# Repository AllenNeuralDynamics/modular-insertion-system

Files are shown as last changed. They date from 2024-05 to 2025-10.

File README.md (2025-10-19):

# Modular Insertion System

A flexible, scalable extracellular electrophysiology rig

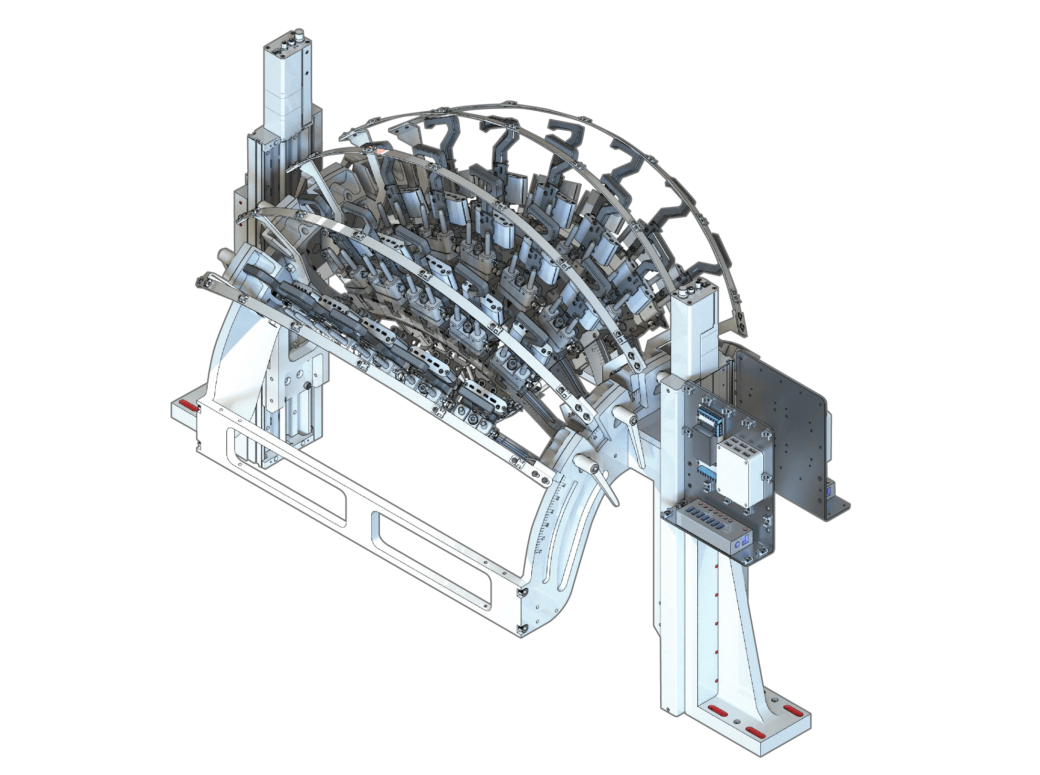
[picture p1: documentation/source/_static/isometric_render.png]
Rendering of the insertion system


## Key features

- Insertion angles up to ±75° A/P and ±45° M/L
- Modules for electrophysiology, optogenetics, and microscopes
- 600 mm x 500 mm open area for behavioral platform
- Design files available for noncommercial use

## Contributors

- Mechanical design: Jon Arnold
- Concept and oversight: Josh Siegle, Karel Svoboda
- Validation: Galen Lynch, Yoni Browning, Anna Lakunina, Xinxin Yin, Han Hou, Susu Chen
- Electrical design: Sonya Vasquez

## How to order

In most cases, we recommend purchasing a [complete system](https://newscaletech.com/modular-insertion-system/) from New Scale Technologies. They can work with you to design a custom configuration to suit your experimental needs.

If you would like to manufacture the individual components, we strongly recommend [posting an issue](https://github.com/AllenNeuralDynamics/modular-insertion-system/issues) before getting started so we can provide advice on the best way forward. We offer no guarantees that the system will work as advertised if you assemble it on your own.

## Documentation

We may decide to launch a web-based documentation site at some point. To build the documentation yourself, follow these instructions:

First, make sure [Sphinx](https://www.sphinx-doc.org/en/master/usage/installation.html) is installed on your system.

Then, in a Python virtual environment (e.g. `conda`), run

```
pip install -e .[docs]
```

To create the documentation HTML files, run

```
sphinx-build -b html documentation/source/ documentation/build/html
```

## License

The contents of this repository are covered by the [Creative Commons BY-NC-SA License](LICENSE). Any design files or documentation, or modifications thereof, cannot be used for commercial purposes without prior written consent from the Allen Institute. In other words, you are allowed to build the system for use in your own lab, but you cannot sell the drawings, models, or physical components. Any derivations must be attributed to the Allen Institute and shared with the same licensing terms.



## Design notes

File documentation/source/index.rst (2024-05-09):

Modular Insertion System
===========================================

Rendering of the insertion system

.. toctree::
   :maxdepth: 2
   :caption: Contents:

   design
   modules
   components
   configurations
   protocols
   ordering

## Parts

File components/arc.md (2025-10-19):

# Arc

Each arc supports up to 7 modules. Quantities are per arc.

## Custom Machined Parts

|  Description              |  Part #   |  Quantity   |
| ------------------------- | --------- | ----------- |
|  Sliding Ring             | J009968   | 1           |
|  Arc Adjust               | J009962   | 1           |
|  Arc Adjust Mirror        | J009963   | 1           |
|  Arc Clamp                | J009970   | 2           |
|  Arc Trellis              | 51014     | 1           |
|  Arc Trellis Mount        | 51015     | 1           |
|  Arc Trellis Mount Mirror | 51013     | 1           |

## McMaster Parts

|  Description                         |  Part #    |  Quantity   |
| ------------------------------------ | ---------  | ----------- |
|  3/16 x 3/4L Dowel Pin               | 90145A508  | 1           |
|  Plastic Adjustable-Position Handle  | 5101K26    | 2           |
|  5/16 x 1-14L SCHS SS                | 92196A585  | 4           |
|  5/16 Nut SS                         | 91845A030  | 4           |
|  M4 Washer SS                        | 93475A230  | 4           |
|  M4 x 5 BHCS SS                      | 92095A477  | 6           |
|  M4 x 8 BHCS SS                      | 92095A189  | 4           |
|  Cable Tie Mount                     | 7566K28    | 6           |

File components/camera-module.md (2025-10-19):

# Camera Module

Used to visualize the insertion area. Quantities are per module.

## Custom Machined Parts

|  Description              |  Part #   |  Quantity   |
| ------------------------- | --------- | ----------- |
|  Camera Module Cap        | 51019     | 1           |
|  Gonio Mount Plate        | J010017   | 1           |
|  WD Adjust Plate          | J009975   | 1           |
|  Focus Motor Mount        | J010016   | 1           |
|  Focus Motor Bracket      | J009974   | 1           |

## McMaster Parts

|  Description                         |  Part #    |  Quantity   |
| ------------------------------------ | ---------  | ----------- |
|  M2 x 4 SHCS SS                      | 91292A004  | 2           |
|  M3 x 4 SHCS SS                      | 91292A109  | 3           |
|  M3 x 6 SHCS SS                      | 91292A111  | 9           |
|  M3 x 8 SHCS SS                      | 91292A112  | 2           |
|  M4 x 5 SHCS SS                      | 91292A105  | 8           |
|  M3 x 8 Flat Head Cap Screw          | 92125A128  | 7           |
|  M3 x 10 Flat Head Cap Screw         | 92125A130  | 4           |
|  10-32 x 3/8 Nylon Thumb Screw       | 94323A727  | 1           |
|  10-32 x 1/4 Spring Plunger          | 94323A727  | 1           |

## Edmund Optics Parts

|  Description                         |  Part #    |  Quantity   |
| ------------------------------------ | ---------  | ----------- |
|  FLIR Blackfly USB Camera            | 11-516     | 1           |
|  InfiniProbe S-25 Video Microscope   | 58-806     | 1           |
|  CS to C Mount, 5 mm Spacer          | 03-618     | 1           |

## Misumi Parts

|  Description                         |  Part #      |  Quantity   |
| ------------------------------------ | -----------  | ----------- |
|  Goniometer                          | GFG40-25     | 1           |
|  Dovetail Stage                      | XFHT40       | 1           |
|  Dovetail Stage                      | XSLC60       | 1           |
|  Precision Washer 14 OD 8 ID 2 THK   | WSSS14-8-2   | 1           |
|  M8 x 40 SHCS Captive Low Head SS    | GUTBT8-10-40 | 1           |
|  Flat Belt Pulley                    | HBPUS15-P6-6 | 1           |

## Panduit Parts

|  Description                         |  Part #    |  Quantity   |
| ------------------------------------ | ---------  | ----------- |
|  Cable Tie Mount                     |  TM1S4-M   | 4           |

## SDP-SI Parts

|  Description                         |  Part #         |  Quantity   |
| ------------------------------------ | --------------  | ----------- |
|  Bore Reducer (6 mm to 3 mm)         | A 7A30M060309   | 1           |

## Polulu Parts (for optional focus motor)

|  Description                         |  Part #    |  Quantity   |
| ------------------------------------ | ---------  | ----------- |
|  Gearmotor Bracket                   | 1086       | 1           |
|  Gearmotor HPCB 12V 380:1 Ext Shaft  | 4799       | 1           |
|  Magnetic Encoder                    | 4760       | 1           |

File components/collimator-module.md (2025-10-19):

# Collimator Module

Holds a collimator for optogenetic stimulation. Quantities are per module.

## Custom Machined Parts

|  Description              |  Part #     |  Quantity   |
| ------------------------- | ----------- | ----------- |
|  Collimator Module Cap    | 51017       | 1           |
|  Spacer Block             | J010039     | 1           |
|  Handle                   | J009927     | 1           |
|  Cable Cover              | J009976     | 1           |
|  Collimator Clamp         | J010040     | 1           |
|  Collimator Mount         | J010042     | 1           |
|  Collimator Cover         | J010043     | 1           |

## McMaster Parts

|  Description                           |  Part #    |  Quantity   |
| -------------------------------------- | ---------  | ----------- |
|  M1.6 x 3 SHCS SS                      | 92290A596  | 3           |
|  M1.6 x 4 SHCS SS                      | 91292A261  | 7           |
|  M1.6 x 5 SHCS SS                      | 91292A262  | 8           |
|  M1.6 x 10 SHCS SS                     | 92290A602  | 2           |
|  M2 x 10 SHCS SS                       | 91292A833  | 4           |
|  M2.5 x 10 PHMS SS                     | 92000A106  | 1           |
|  M3 x 8 SHCS SS                        | 92192A112  | 9           |
|  M4 x 12 SHCS SS                       | 91292A117  | 2           |
|  M8 x 40 Captive Screw SS              | 95966A713  | 1           |
|  8-32 x 5/8 L FHMS SS                  | 94323A727  | 1           |
|  10-32 x 3/8 Nylon Thumb Screw         | 91771A196  | 1           |
|  10-32 x 1/4 Spring Plunger            | 8691A312   | 1           |
|  Spacer                                | 92510A533  | 1           |
|  Size 10 O-Ring                        | 9452K18    | 1           |
|  Indicating Knob (modified as J009972) | 6094K18    | 1           |

## New Scale Parts

|  Description                         |  Part #                |  Quantity   |
| ------------------------------------ | ---------------------  | ----------- |
|  XYZ Stage Assembly                  | M3-LS-3.4-15-XYZ-MIS   | 1           |

## Thorlabs Parts

|  Description                         |  Part #      |  Quantity   |
| ------------------------------------ | -----------  | ----------- |
|  Fiber Optic Collimator              | CFC2-A       | 1           |

## Misumi Parts

|  Description                         |  Part #      |  Quantity   |
| ------------------------------------ | -----------  | ----------- |
|  Precision Washer 14 OD 8 ID 2 THK   | WSSS14-8-2   | 1           |

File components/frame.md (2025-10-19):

# Frame

Each frame supports up to 11 sliding arcs. One frame is needed for each rig.

## Custom Machined Parts

|  Description              |  Part #     |  Quantity   |
| ------------------------- | ----------- | ----------- |
|  Elevator Side Spacer     | J009953     | 2           |
|  Stage to Frame Connector | J009954     | 2           |
|  Side Arc                 | J009955     | 2           |
|  Connector Bar            | J009956     | 2           |
|  Angle Plate              | J009946     | 2           |
|  Mounting Bracket         | 0295-100-01 | 2           |

## Vertical Translation Stage

|  Description                      |  Vendor   |  Part #            |  Quantity   |
| --------------------------------- | --------- | ------------------ | ----------- |
|  Linear Ball Screw Stage, 450 mm  | Zaber     | LRQ450HL-DE51T10A  | 2           |
|  2 Axis Controller                | Zaber     | X-MCC2-KX15B       | 1           |
|  Cable, 1.5 m                     | Zaber     | MC10               | 1           |

## McMaster Parts

|  Description                         |  Part #    |  Quantity   |
| ------------------------------------ | ---------  | ----------- |
|  3/16 x 3/4L Dowel Pin               | 90145A508  | 16          |
|  5/16"-18 x 3/4" SHCS SS             | 92196A581  | 24          |
|  1/4"-20 x 7/16" Low Head SHCS SS    | 93615A409  | 40          |
|  M6 x 14 SHCS SS                     | 91292A070  | 4           |
|  M4 x 5 BHCS SS                      | 92095A477  | 32          |
|  M3 x 8 BHCS SS                      | 92095A181  | 16          |

## USB Hub (StarTech)

|  Description                         |  Part #    |  Quantity   |
| ------------------------------------ | ---------  | ----------- |
|  7-Port USB 3.0 Hub                  | ST7300U3M  | 2           |

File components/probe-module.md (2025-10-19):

# Probe Module

Holds a probe for recording. Quantities are per module.

## Custom Machined Parts

|  Description              |  Part #     |  Quantity   |
| ------------------------- | ----------- | ----------- |
|  Probe Module Cap         | 51017       | 1           |
|  Spacer Block             | J008605     | 1           |
|  Handle                   | J009927     | 1           |
|  Indicator Dial           | J009971     | 1           |
|  Cable Cover              | J009976     | 1           |
|  Interconnect Panel       | 0295-250-01 | 1           |
|  Probe Clamp Base         | 0295-251-01 | 1           |
|  Probe Clamp Hinge        | 0295-251-02 | 1           |
|  Mounting Rod             | J010091     | 1           |

## McMaster Parts

|  Description                           |  Part #    |  Quantity   |
| -------------------------------------- | ---------  | ----------- |
|  M1.6 x 3 SHCS SS                      | 92290A596  | 3           |
|  M1.6 x 4 SHCS SS                      | 91292A261  | 7           |
|  M1.6 x 5 SHCS SS                      | 91292A262  | 8           |
|  M2 x 2.5 SHCS SS                      | 92000A106  | 1           |
|  M2 x 6 FHMS SS                        | 91305A105  | 1           |
|  M2 x 10 SHCS SS                       | 92605A712  | 4           |
|  M3 x 8 SHCS SS                        | 92192A112  | 9           |
|  M4 x 12 SHCS SS                       | 91292A117  | 2           |
|  M8 x 40 Captive Screw SS              | 95966A713  | 1           |
|  8-32 x 7/8 L FHMS SS                  | 91771A198  | 1           |
|  10-32 x 3/8 Nylon Thumb Screw         | 91771A196  | 1           |
|  10-32 x 1/4 Spring Plunger            | 8691A312   | 1           |
|  M2.5 x 20 Dowel Pin                   | 91585A310  | 1           |
|  Indicating Knob (modified as J009972) | 6094K18    | 1           |

## New Scale Parts

|  Description                         |  Part #                |  Quantity   |
| ------------------------------------ | ---------------------  | ----------- |
|  XYZ Stage Assembly                  | M3-LS-3.4-15-XYZ-MIS   | 1           |

## Misumi Parts

|  Description                         |  Part #      |  Quantity   |
| ------------------------------------ | -----------  | ----------- |
|  Precision Washer 14 OD 8 ID 2 THK   | WSSS14-8-2   | 1           |
|  M3 x 10 Captive SHCS SS             | GUTB3-4-10   | 1           |

## Panduit Parts

|  Description                         |  Part #    |  Quantity   |
| ------------------------------------ | ---------  | ----------- |
|  Cable Tie Mount                     | TM1S4      | 4           |

## Digi-Key Parts

|  Description                         |  Part #    |  Quantity   |
| ------------------------------------ | ---------  | ----------- |
|  Banana Jack Connector               | J153-ND    | 2           |

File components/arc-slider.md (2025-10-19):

# Arc Slider

Connects modules to an arc. One arc slider per module.

## Custom Machined Parts

|  Description              |  Part #   |  Quantity   |
| ------------------------- | --------- | ----------- |
|  Carriage                 | 51018     | 1           |
|  Cover                    | 51016     | 1           |

## McMaster Parts

|  Description                         |  Part #    |  Quantity   |
| ------------------------------------ | ---------  | ----------- |
|  Guide Pin (modified as J009515)     | 97355A439  | 2           |
|  M3 x 10 SHCS SS Low Head            | 92855A310  | 2           |
|  M3 x 18 SHCS SS                     | 92855A510  | 2           |
|  M5 x 10 SHCS SS Low Head            | 91292A029  | 2           |

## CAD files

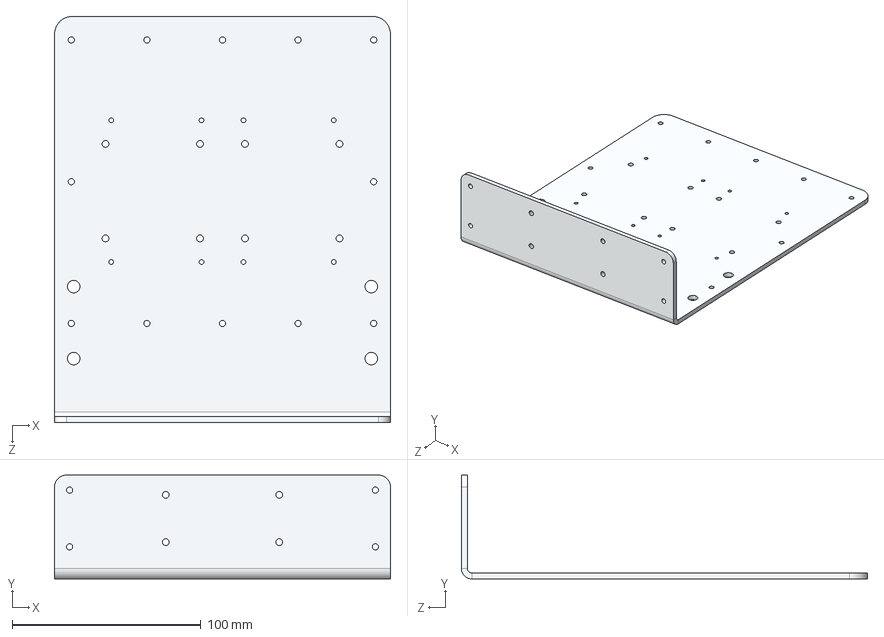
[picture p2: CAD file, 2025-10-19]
models/frame/0295-100-01 Mounting Bracket.step
177.8 x 55.0 x 215.0 mm

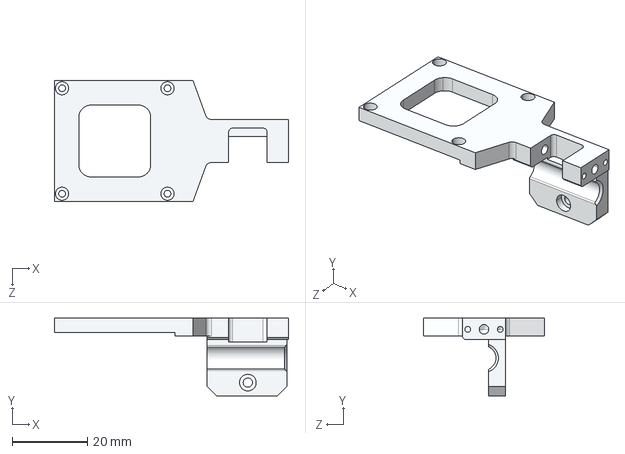
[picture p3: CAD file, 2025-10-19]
models/probe-module/0295-251-01 Probe Clamp Base.step
62.1 x 20.7 x 32.0 mm

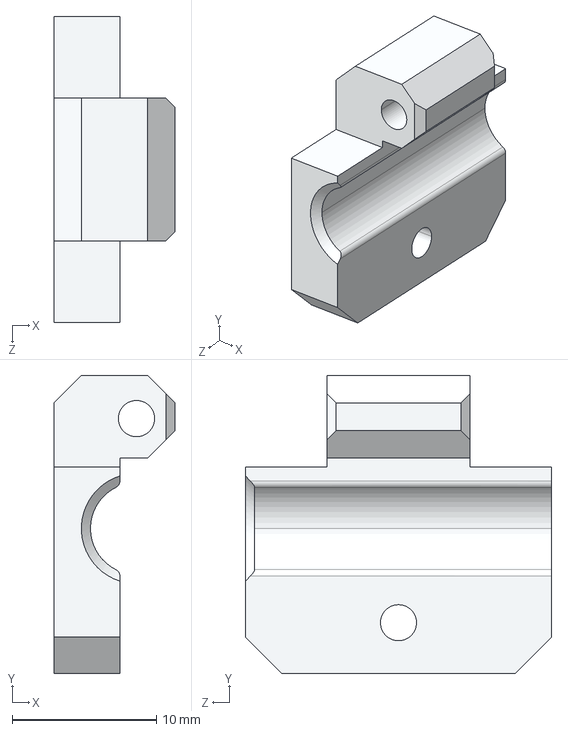
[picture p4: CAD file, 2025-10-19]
models/probe-module/0295-251-02 Probe Clamp Hinge.step
8.38 x 20.7 x 21.2 mm

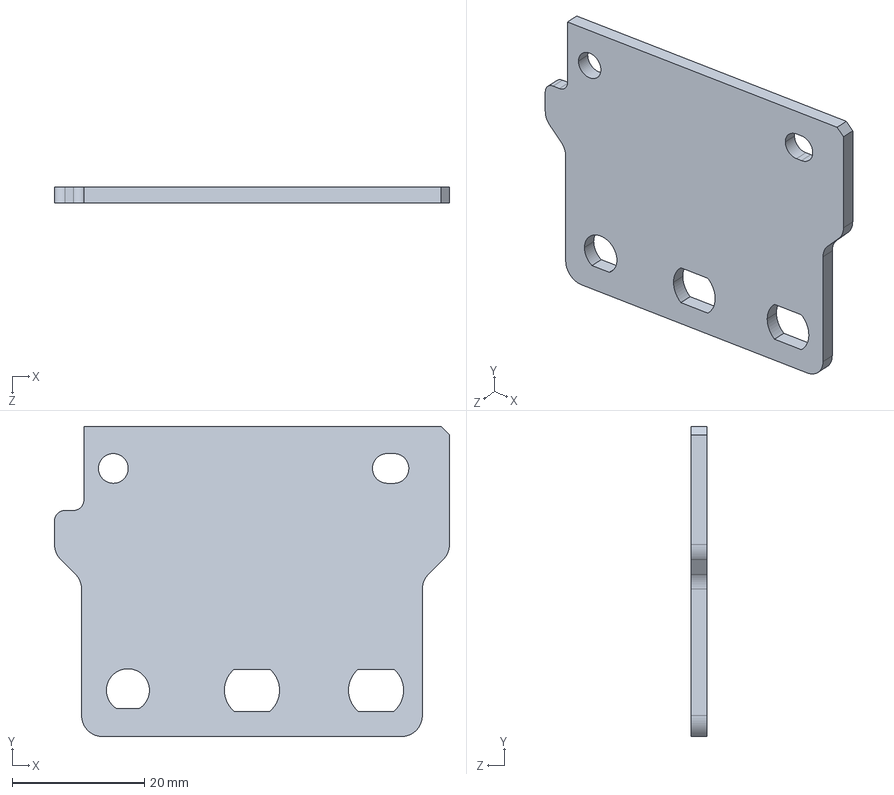
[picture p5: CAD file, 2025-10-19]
models/probe-module/0295-250-01 Probe Module Interconnect.step
59.7 x 46.9 x 2.38 mm

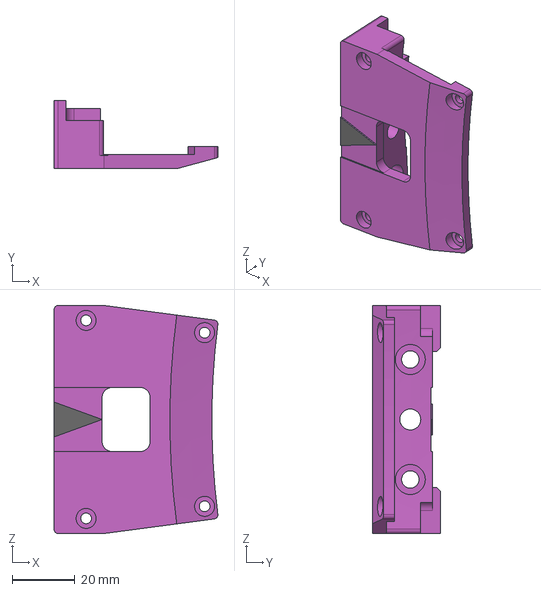
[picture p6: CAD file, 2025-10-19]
models/arc-slider/51018 Carriage.step
52.0 x 21.7 x 72.4 mm

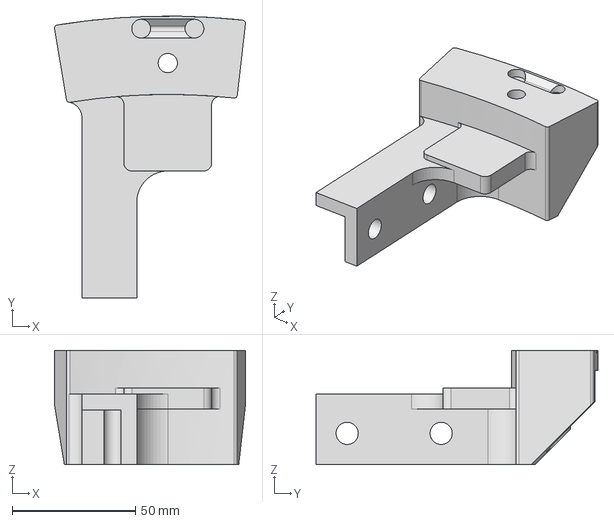
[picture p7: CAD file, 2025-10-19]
models/arc/J009962 Arc Adjust.step
77.4 x 114.2 x 46.4 mm

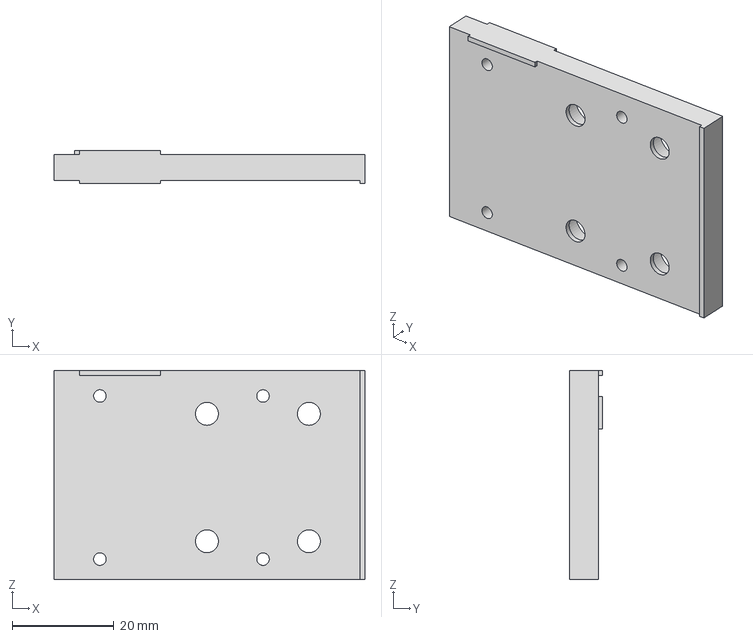
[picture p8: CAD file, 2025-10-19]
models/camera-module/J010017 Gonio Mount Plate.step
61.0 x 6.48 x 41.0 mm

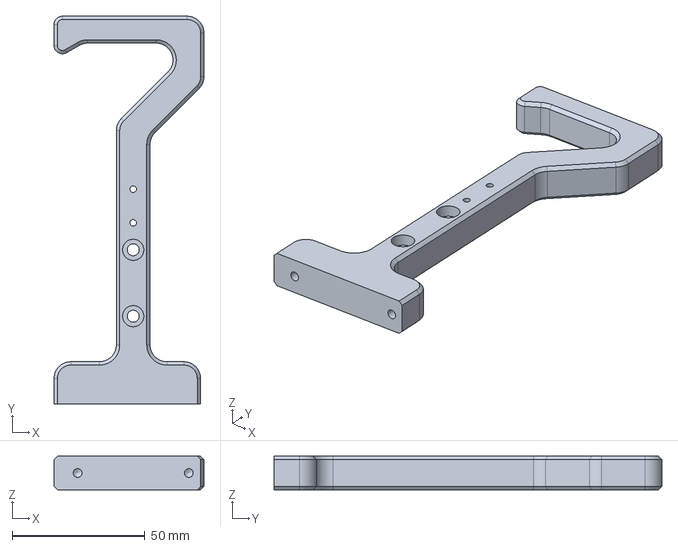
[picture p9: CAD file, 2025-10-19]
models/collimator-module/J009927 Handle.step
56.5 x 146.0 x 12.7 mm

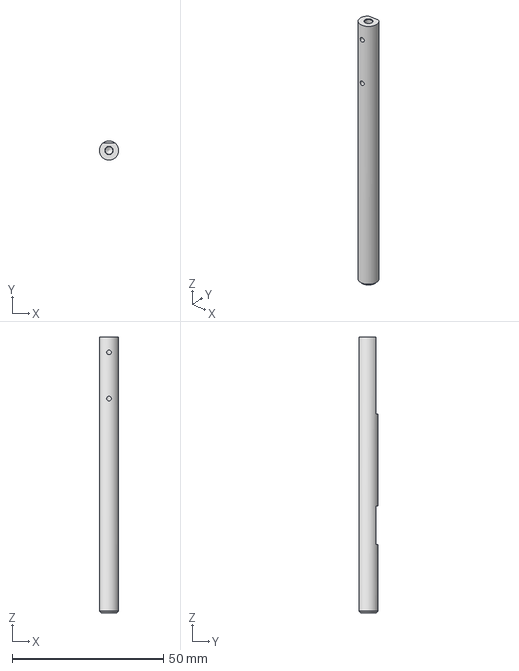
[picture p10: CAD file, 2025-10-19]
models/probe-module/J010091 Mounting Rod.step
6.35 x 6.35 x 91.1 mm

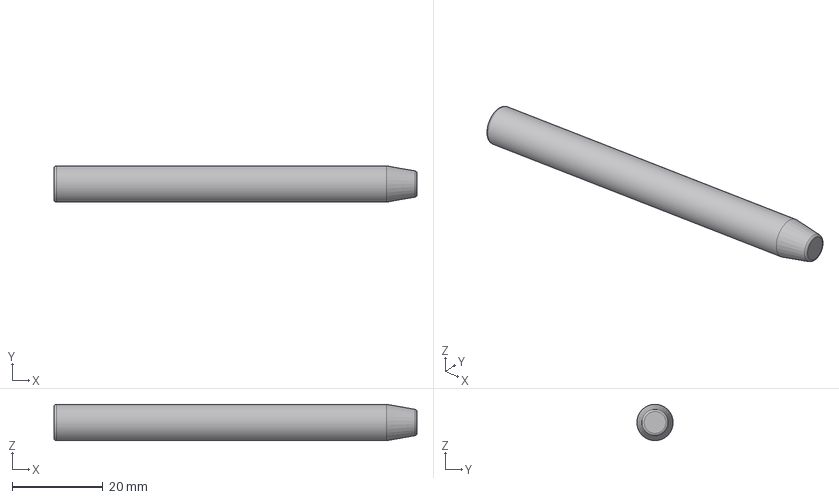
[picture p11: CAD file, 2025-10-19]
models/arc-slider/J009515 Guide Pin.step
80.0 x 8.00 x 7.99 mm

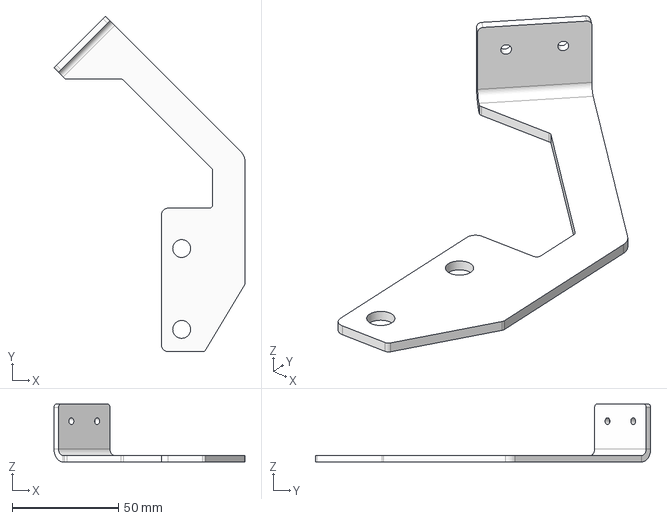
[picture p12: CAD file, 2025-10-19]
models/arc/51014 Arc Trellis Mount.step
90.0 x 158.1 x 27.3 mm

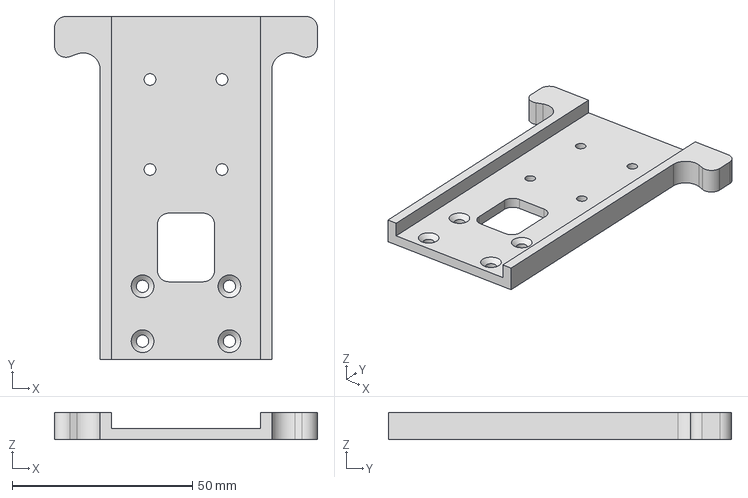
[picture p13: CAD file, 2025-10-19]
models/camera-module/J009975 WD Adjust Plate.step
73.0 x 95.2 x 7.62 mm

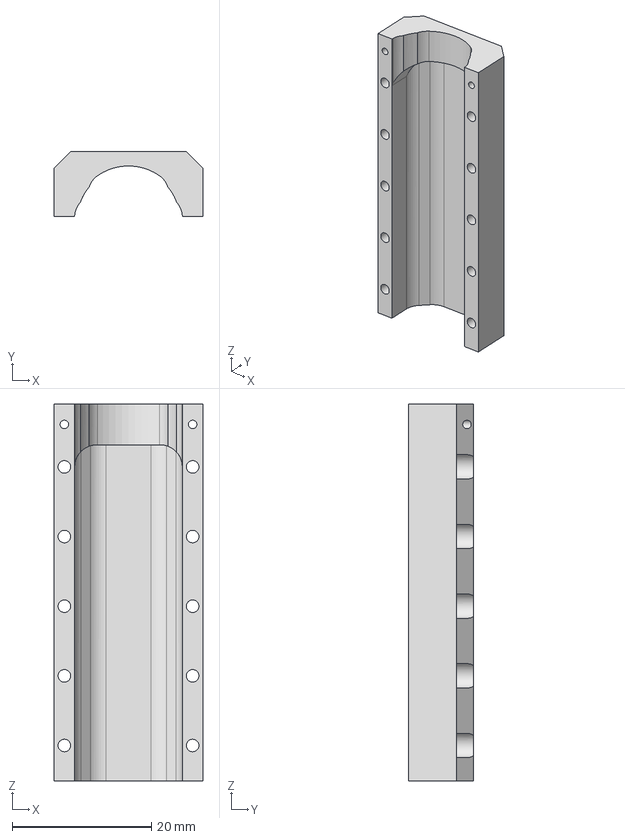
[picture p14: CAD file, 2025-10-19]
models/collimator-module/J010043 Collimator Cover.step
21.4 x 9.39 x 54.1 mm

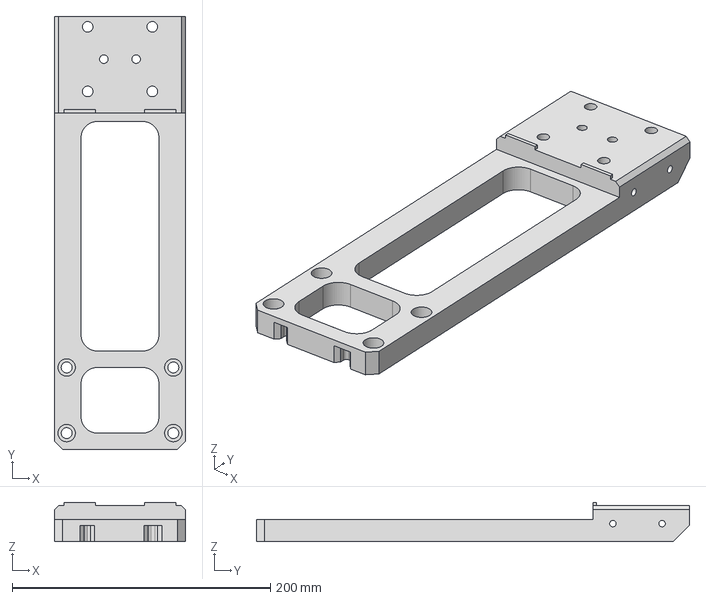
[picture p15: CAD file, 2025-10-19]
models/frame/J009954 Stage to Frame Connector.step
101.6 x 335.1 x 30.5 mm

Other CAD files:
models/probe-module/J009976 Cable Cover.step
models/arc-slider/51016 Cover.step
models/arc/51015 Arc Trellis Mount Mirror.step
models/camera-module/51019 Camera Module Cap.step
models/arc/51013 Arc Trellis.dxf
models/arc/51014 Arc Trellis Mount.dxf
models/arc/51015 Arc Trellis Mount Mirror.dxf
models/arc/J009963 Arc Adjust Mirror.step
models/arc/J009970 Arc Clamp.step
models/camera-module/J009974 Focus Motor Bracket.step
models/camera-module/J010016 Focus Motor Mount.step
models/collimator-module/51017 Collimator Module Cap.step
models/collimator-module/J009976 Cable Cover.step
models/collimator-module/J010039 Spacer Block.step
models/collimator-module/J010040 Collimator Clamp.step
models/collimator-module/J010042 Collimator Mount.step
models/frame/J009946 Angle Plate.step
models/frame/J009953 Elevator Side Spacer.step
models/frame/J009956 Connector Bar.step
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

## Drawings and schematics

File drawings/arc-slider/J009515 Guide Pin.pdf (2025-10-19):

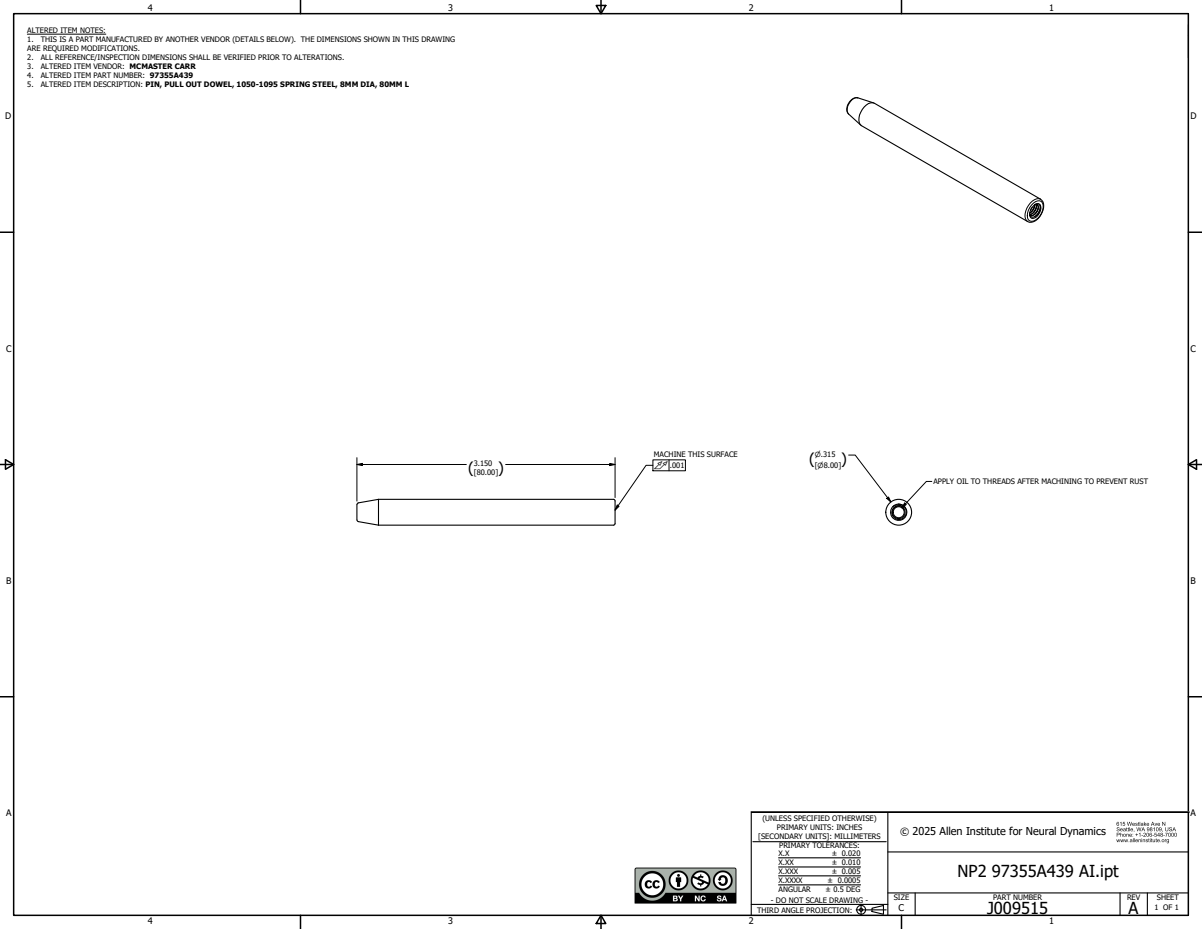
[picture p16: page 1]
SIZE; PART NUMBER; REV; SHEET; 1 OF 1 THIRD ANGLE PROJECTION:; ± 0.020 ± 0.010 ± 0.005 ± 0.0005 ± 0.5 DEG; ) MACHINE THIS SURFACE

ALTERED ITEM NOTES:
1. THIS IS A PART MANUFACTURED BY ANOTHER VENDOR (DETAILS BELOW). THE DIMENSIONS SHOWN IN THIS DRAWING
ARE REQUIRED MODIFICATIONS.
2. ALL REFERENCE/INSPECTION DIMENSIONS SHALL BE VERIFIED PRIOR TO ALTERATIONS.
3. ALTERED ITEM VENDOR: MCMASTER CARR
4. ALTERED ITEM PART NUMBER: 97355A439
5. ALTERED ITEM DESCRIPTION: PIN, PULL OUT DOWEL, 1050-1095 SPRING STEEL, 8MM DIA, 80MM L

APPLY OIL TO THREADS AFTER MACHINING TO PREVENT RUST

(UNLESS SPECIFIED OTHERWISE)
PRIMARY UNITS: INCHES
[SECONDARY UNITS]: MILLIMETERS
PRIMARY TOLERANCES:
X.XXX
X.XXXX
ANGULAR
- DO NOT SCALE DRAWING -

© 2025 Allen Institute for Neural Dynamics
NP2 97355A439 AI.ipt

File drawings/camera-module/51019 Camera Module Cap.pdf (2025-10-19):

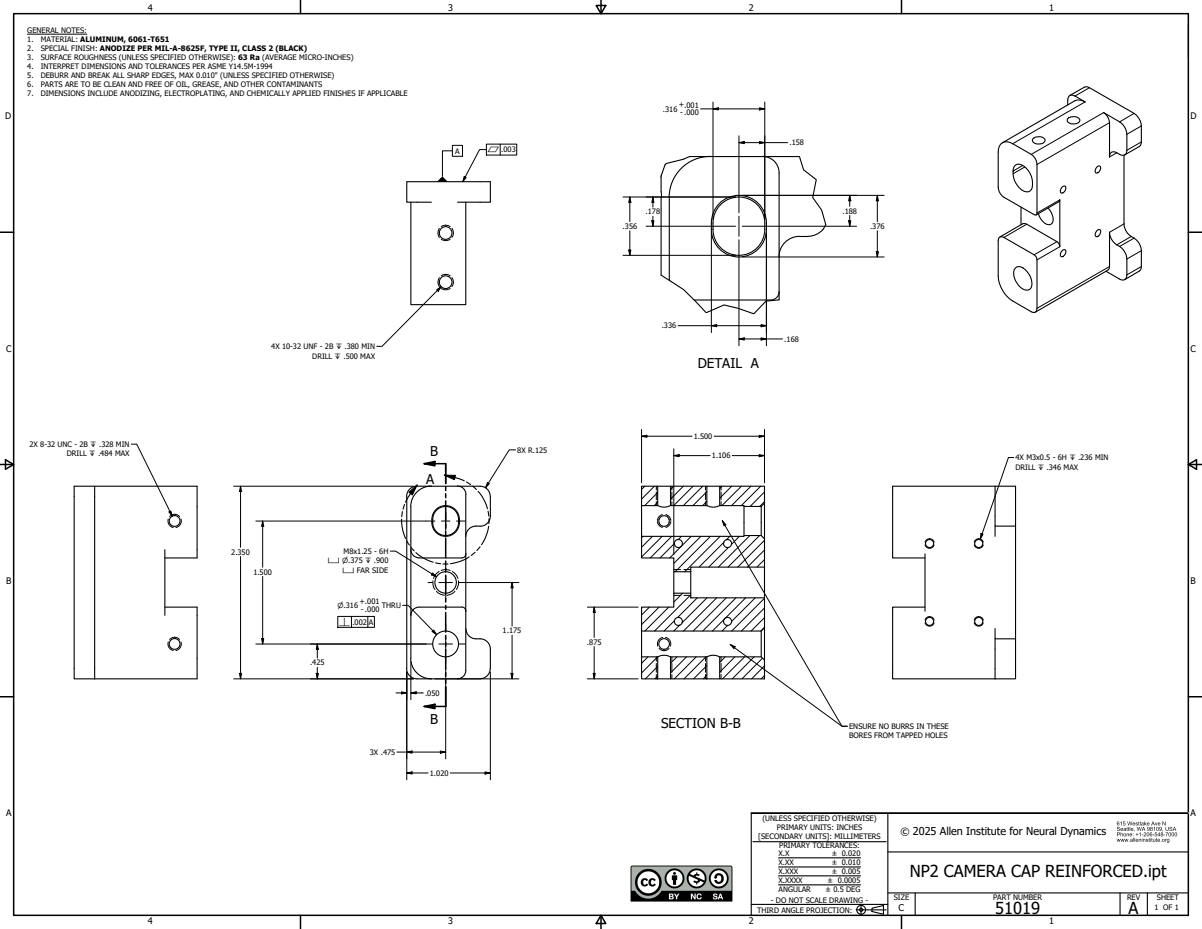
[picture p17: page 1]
DETAIL A; SECTION B-B; SIZE; PART NUMBER; REV; SHEET; 1 OF 1 THIRD ANGLE PROJECTION:; ± 0.020 ± 0.010 ± 0.005 ± 0.0005 ± 0.5 DEG; +.001 THRU

GENERAL NOTES:
1. MATERIAL: ALUMINUM, 6061-T651
2. SPECIAL FINISH: ANODIZE PER MIL-A-8625F, TYPE II, CLASS 2 (BLACK)
3. SURFACE ROUGHNESS (UNLESS SPECIFIED OTHERWISE): 63 Ra (AVERAGE MICRO-INCHES)
4. INTERPRET DIMENSIONS AND TOLERANCES PER ASME Y14.5M-1994
5. DEBURR AND BREAK ALL SHARP EDGES, MAX 0.010" (UNLESS SPECIFIED OTHERWISE)
6. PARTS ARE TO BE CLEAN AND FREE OF OIL, GREASE, AND OTHER CONTAMINANTS
7. DIMENSIONS INCLUDE ANODIZING, ELECTROPLATING, AND CHEMICALLY APPLIED FINISHES IF APPLICABLE

ENSURE NO BURRS IN THESE
BORES FROM TAPPED HOLES

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

© 2025 Allen Institute for Neural Dynamics
NP2 CAMERA CAP REINFORCED.ipt

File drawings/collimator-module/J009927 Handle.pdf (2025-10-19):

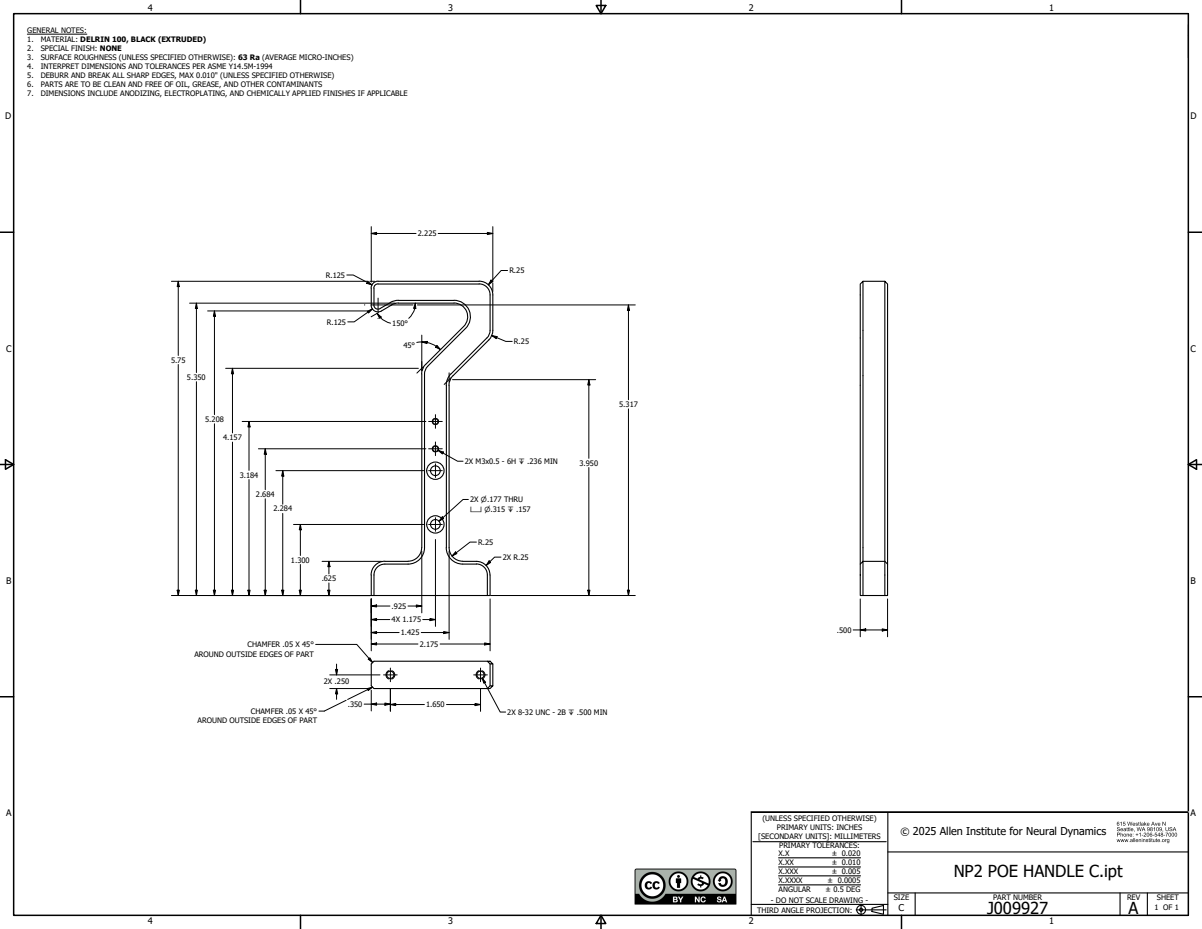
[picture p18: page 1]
SIZE; PART NUMBER; REV; SHEET; 1 OF 1 THIRD ANGLE PROJECTION:; ± 0.020 ± 0.010 ± 0.005 ± 0.0005 ± 0.5 DEG; CHAMFER .05 X 45°

GENERAL NOTES:
1. MATERIAL: DELRIN 100, BLACK (EXTRUDED)
2. SPECIAL FINISH: NONE
3. SURFACE ROUGHNESS (UNLESS SPECIFIED OTHERWISE): 63 Ra (AVERAGE MICRO-INCHES)
4. INTERPRET DIMENSIONS AND TOLERANCES PER ASME Y14.5M-1994
5. DEBURR AND BREAK ALL SHARP EDGES, MAX 0.010" (UNLESS SPECIFIED OTHERWISE)
6. PARTS ARE TO BE CLEAN AND FREE OF OIL, GREASE, AND OTHER CONTAMINANTS
7. DIMENSIONS INCLUDE ANODIZING, ELECTROPLATING, AND CHEMICALLY APPLIED FINISHES IF APPLICABLE

AROUND OUTSIDE EDGES OF PART

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

© 2025 Allen Institute for Neural Dynamics
NP2 POE HANDLE C.ipt

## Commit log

2025-10-19 Add parts lists for probe, collimator, and camera modules
2025-10-19 Add 3D models
    [0295-100-01 Mounting Bracket.step, 0295-250-01 Probe Module Interconnect.step, 0295-251-01 Probe Clamp Base.step, 0295-251-02 Probe Clamp Hinge.step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]
